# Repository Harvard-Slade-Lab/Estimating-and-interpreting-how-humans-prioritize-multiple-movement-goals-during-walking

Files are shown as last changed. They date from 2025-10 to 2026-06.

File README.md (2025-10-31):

# Estimating-and-interpreting-how-humans-prioritize-multiple-movement-goals-during-walking
Materials, data, and code needed to reproduce "Estimating and interpreting how humans prioritize multiple movement goals during walking" study.

<ins>ViPer headset materials</ins>

CAD files for the headset, Arduino code, and a BoM are included in this folder.

<ins>Data and code</ins>

Gait metrics analyzed for each step of each condition and averaged across steps are included in this folder. Code to visualize, analyze, and interpret gait metrics is included in this folder. MATLAB 2023b, Jupyter 2025.4.1, and Python 3.12.0 are required to run included code.

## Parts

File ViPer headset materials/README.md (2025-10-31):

Instructions for putting together the ViPer Headset:

1) Print motor_mirror_attachment, panel_behind_fixed_mirror, and bottom_frame using PLA.
2) Laser cut top_frame and frame_headset_interface.
3) Remove the front panel of the Google Daydream View headset.
4) Remove the insert inside the headset that rests on the face.
5) Drill four holes into the outer plastic that align with the four holes in the frame_headset_interface. The part of the headset that protrudes on the bottom should slot right into the interface.
6) Screw the frame_headset_interface onto the headset using the M2.5 screws and secure with hex nuts.
7) Assemble and secure the panel_behind_fixed_mirror, top_frame, and the frame_headset_interface with adhesives of your choice.
8) Attach the smaller mirror to the inside of the panel_behind_fixed_mirror.
9) Cover all holes with construction paper. This is an important step -- the participant's view must be obscured, but the paper ensures that it is a lightweight solution.
10) Insert M3 screw into the hole of the motor_mirror_attachment, such that it portrudes and can fit into the hole in the bottom_frame.
11) Secure the motor_mirror_attachment to the back of the large mirror with adhesives of your choice.
12) Solder the motor, the correct wires, the button, and the resistor to the Arduino UNO shield and attach it to the UNO.
13) Screw the motor onto the top of the ViPer frame using the M4 screws and secure with hex nuts.
14) Attach the motor_mirror_attachment (now attached to the large mirror) to the motor and make sure the M3 screw is dropped directly into the intended hole in the bottom_frame.
15) Secure the Arduino UNO to the top of the headset with adhesives of your choice.
17) Replace the insert inside the headset that rests on the face back inside of the headset.

Optional: If the headset feels unstable or unsecure, print the screw_tube using PLA. Align the tube with the small holes on the top and bottom of the frame next to the servo motor. Take two M2.5 screws and washers and tighten them down to either side of the tube to help hold the headset in place.

ViPer_control.ino is the script used to control the servo mounted to the ViPer headset, and it can be run through Arduino IDE.

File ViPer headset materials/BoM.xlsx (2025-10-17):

Part name | Quantity | Link to purchase | Notes
Google Daydream View headset | 1 | amazon.com/Google-Daydream-View-Headset-Slate/dp/B01N634P7O | Drill four holes to align with frame_headset_interface
Microcontroller | 1 | amazon.com/Arduino-A000066-ARDUINO-UNO-R3/dp/B008GRTSV6/ref=sxin_17_pa_sp_search_thematic_sspa?content-id=amzn1.sym.f3a06935-0d55-4a43-b918-4ea35f8505e5%3Aamzn1.sym.f3a06935-0d55-4a43-b918-4ea35f8505e5&cv_ct_cx=arduino+uno&hvadid=557574772208&hvdev=c&hvex
Servo motor | 1 | https://www.amazon.com/Leapiture-Plastic-Standard-Lightweight-Futaba/dp/B0CL6GTDXS
Large mirror | 1 | https://www.amazon.com/Plymor-Square-Non-Beveled-Glass-Mirror/dp/B0D33QFVSW
Small mirror | 1 | https://www.amazon.com/Juvale-Magnetic-Locker-Mirror-Inches/dp/B07SSSWTPN | Comes in a two pack, but only one is needed
frame_headset_interface | 1 | 3 mm acrylic, cut with laser cutter
top_frame | 1 | 3 mm acrylic, cut with laser cutter
bottom_frame | 1 | 3D printed with PLA
motor_mirror_attachment | 1 | 3D printed with PLA
panel_behind_fixed_mirror | 1 | 3D printed with PLA
M2.5 12mm socket head screws to secure headset | 4 | https://www.mcmaster.com/products/screws/thread-size~m2-5/socket-head-screws-2~/
M4 18mm socket head screws to secure motor | 4 | https://www.mcmaster.com/products/screws/socket-head-screws-2~/alloy-steel-socket-head-screws-8/?s=m4+screws
M3 20 mm socket head screw to secure mirror | 1 | https://www.mcmaster.com/products/screws/socket-head-screws-2~/alloy-steel-socket-head-screws-8/?s=m3+screws
M4 hex nuts for headset screws | 4 | https://www.mcmaster.com/products/hex-nuts/thread-size~m2-5/hex-nuts-2~~/
M4 hex nuts for motor | 4 | https://www.mcmaster.com/products/hex-nuts/thread-size~m4/hex-nuts-5~/hex-nuts-5~hex-nut-profile~standard/
Wires | 5 | https://www.amazon.com/California-JOS-Breadboard-Optional-Multicolored/dp/B0BRTJXND9 | Wires connect Arduino UNO to pushbutton
10k ohm resistor | 1 | https://www.amazon.com/EDGELEC-Resistor-Tolerance-Multiple-Resistance/dp/B07QJB31M7 | Resistor connects to pushbotton
Pushbutton | 1 | https://www.amazon.com/DAOKI-Miniature-Momentary-Tactile-Quality/dp/B01CGMP9GY | Pushbutton allows toggling between perturbation magnitudes
Proto Shield | 1 | https://www.amazon.com/HiLetgo-Prototype-Expansion-Breadboard-ProtoShield/dp/B00HHYBWPO

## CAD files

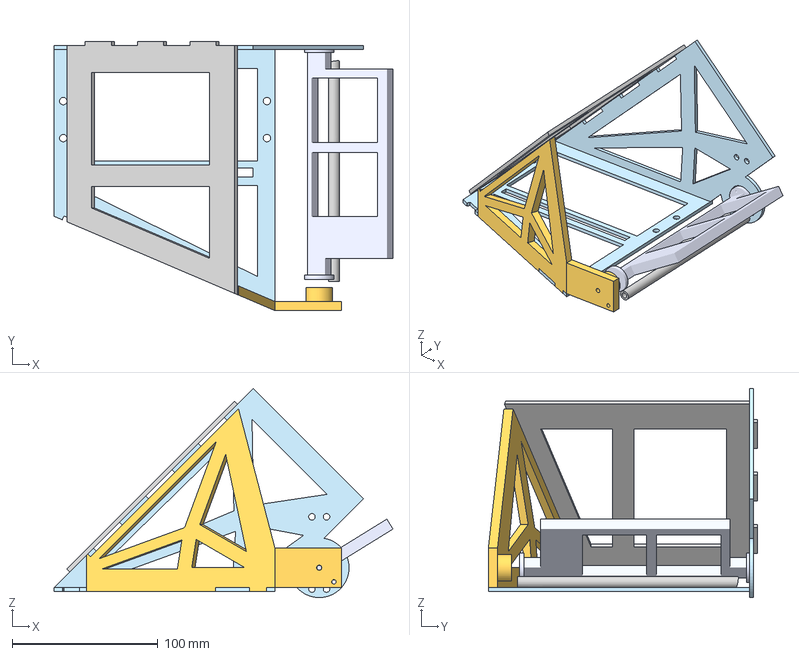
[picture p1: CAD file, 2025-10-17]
ViPer headset materials/CAD files/ViPer_Headset_assembly.step
232.5 x 184.7 x 143.4 mm
top_frame
frame_headset_interface
motor_mirror_attachment
panel_behind_fixed_mirror
bottom_frame
screw_tube

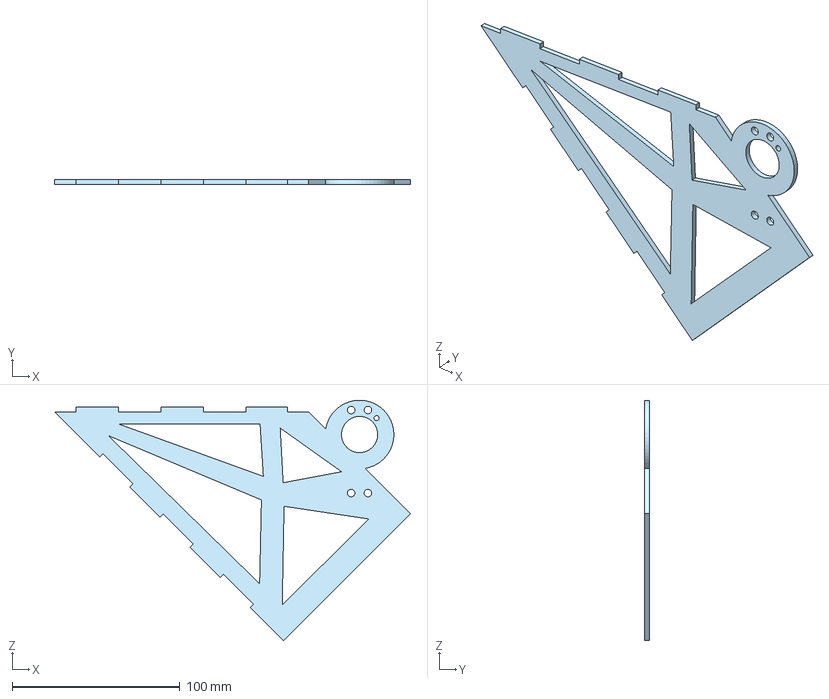
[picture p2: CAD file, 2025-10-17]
ViPer headset materials/CAD files/top_frame.step
212.3 x 2.87 x 143.4 mm

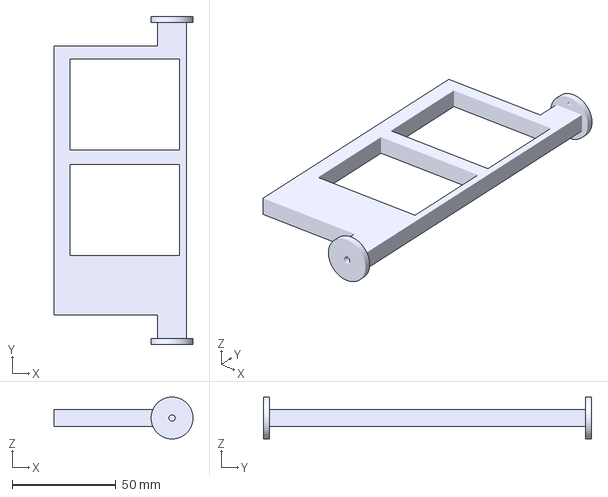
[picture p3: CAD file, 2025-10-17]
ViPer headset materials/CAD files/motor_mirror_attachment.step
67.1 x 158.5 x 20.3 mm

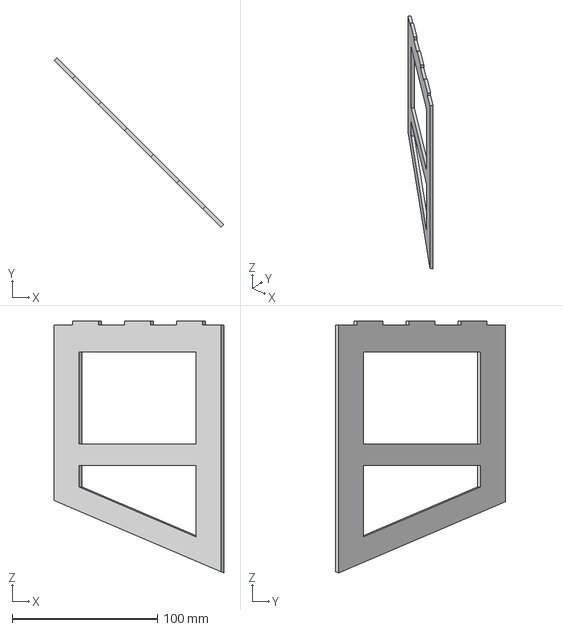
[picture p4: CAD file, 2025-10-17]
ViPer headset materials/CAD files/panel_behind_fixed_mirror.step
117.0 x 117.0 x 173.7 mm

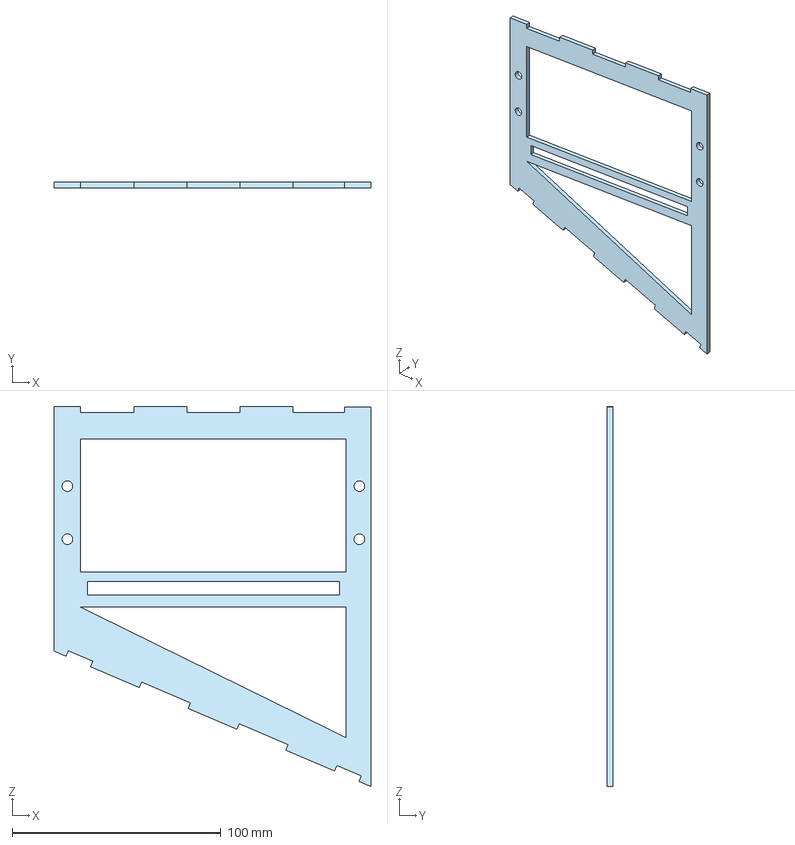
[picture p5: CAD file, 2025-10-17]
ViPer headset materials/CAD files/frame_headset_interface.step
151.5 x 2.87 x 181.8 mm

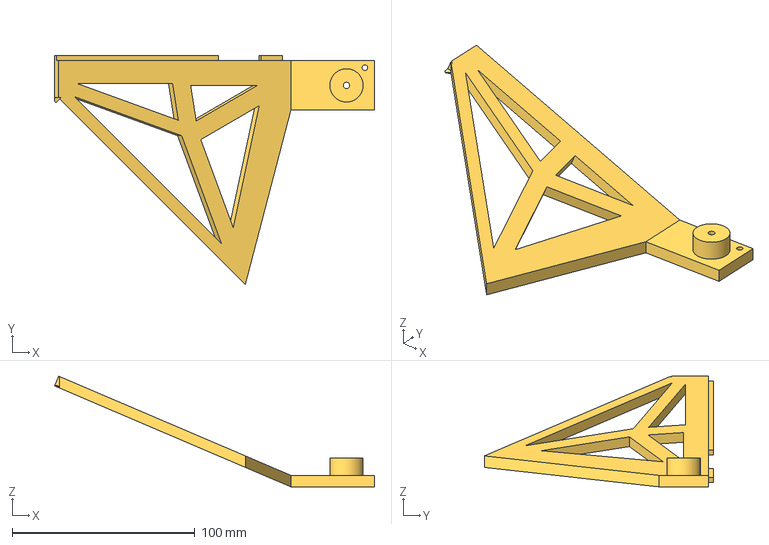
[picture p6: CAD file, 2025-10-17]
ViPer headset materials/CAD files/bottom_frame.step
175.0 x 125.4 x 60.5 mm

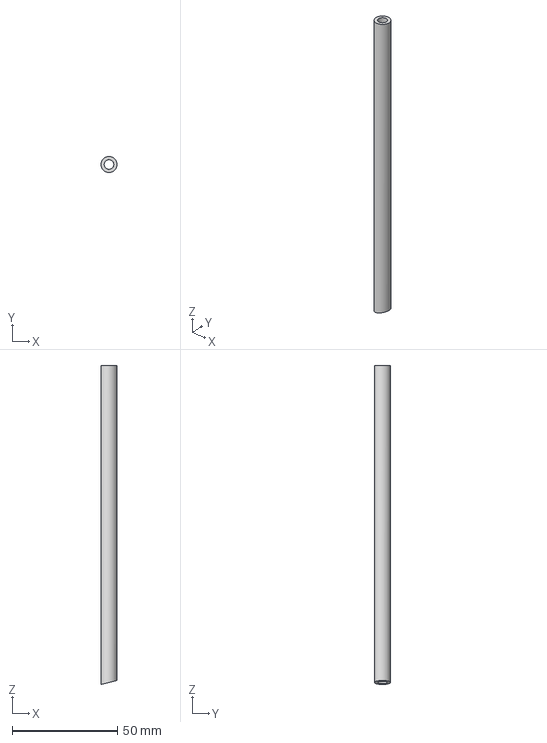
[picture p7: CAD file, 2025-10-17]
ViPer headset materials/CAD files/screw_tube.step
7.62 x 7.62 x 151.6 mm

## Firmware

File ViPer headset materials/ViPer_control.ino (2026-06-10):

#include <Servo.h>

Servo myservo;  // create servo object 

unsigned long startMillis;
const int servoPin = 10;
const int buttonPin = 2;  // button connected to pin 2
int buttonState = 0;      // current state of the button
int lastButtonState = 0;  // previous state of the button
int buttonPushCounter = 0; // counter for the number of button presses
unsigned long lastDebounceTime = 0;  // the last time the output pin was toggled
unsigned long debounceDelay = 50;    // the debounce time; increase if the output flickers
bool returningToZero = true; // flag to handle initial movement to zero position
int lastPos = 0; 

void setup() {
  Serial.begin(115200);         // initialize serial communication at 115200 bits per second
  myservo.attach(servoPin);     // attaches the servo on pin 10 to the servo object
  pinMode(buttonPin, INPUT);    // initialize the button pin as an input
  startMillis = millis();       // record the start time           // start at the neutral position
}

void loop() {

  // read the state of the switch into a local variable
  int reading = digitalRead(buttonPin);

  // check if the button state has changed
  if (reading != lastButtonState) {
    lastDebounceTime = millis(); // reset the debouncing timer
  }

  if ((millis() - lastDebounceTime) > debounceDelay) {
    // if the button state has changed:
    if (reading != buttonState) {
      buttonState = reading;

      // only toggle the counter if the new button state is HIGH
      if (buttonState == HIGH) {
        buttonPushCounter++;
        if (buttonPushCounter > 3) {
          buttonPushCounter = 0; // reset counter after 3 presses
        }
      }
    }
  }

  // save the reading. Next time through the loop, it'll be the lastButtonState:
  lastButtonState = reading;

  unsigned long currentMillis = millis();
  float t = (currentMillis - startMillis) / 1000.0;  // convert milliseconds to seconds
  float pos = 120; // default position

  // Select expression based on the number of button presses
  if (buttonPushCounter == 1) {
    // Low perturbation magnitude
    pos = 115 + 12.5*(0.5*sin(M_PI * 2 * 0.25 * t) + 0.25 * sin(M_PI * 2 * 0.125 * t) + 0.25 * sin(M_PI * 2 * 0.442 * t));
  } else if (buttonPushCounter == 2) {
    // High perturbation magnitude
    pos = 115 + 25*(0.5*sin(M_PI * 2 * 0.25 * t) + 0.25 * sin(M_PI * 2 * 0.125 * t) + 0.25 * sin(M_PI * 2 * 0.442 * t));
  } else if (buttonPushCounter == 3) {
    // Zero perturbation magnitude
    pos = 120; // Neutral
  }
//135
  // Ensure the position is within the valid range 
  pos = constrain(pos, 77, 133);

  // Only update the servo if the position has changed
  if (pos != lastPos) {
    myservo.write(pos);  // update the servo position
    lastPos = pos; // save the current position
  }
  
  myservo.write(pos);  // update the servo position
  
  // Print the position to the Serial Monitor
  Serial.print("Time: ");
  Serial.print(t);
  Serial.print(" s, Position: ");
  Serial.print(pos);
  Serial.print(" Button Presses: ");
  Serial.println(buttonPushCounter);
  
  Serial.println(pos);
  delay(15);  // small delay to smooth out the motion
}

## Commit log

2025-10-03 Create Bill of materials
2025-10-03 Rename Bill of materials to Bill of materials
2025-10-17 Add assembly instructions to README for ViPer Headset
    Added detailed assembly instructions for the ViPer Headset.
2025-10-27 Rename Step-to-step data and code/data_BMH01_test.xlsx to Step-to-step data and code/Averages per trial/data_BMH01_test.xlsx
    [data_BMH01_test.xlsx]
2025-10-27 Rename Step-to-step data and code/data_BMH02_test.xlsx to Step-to-step data and code/Averages per trial/data_BMH02_test.xlsx
    [data_BMH02_test.xlsx]
2025-10-27 Rename Step-to-step data and code/data_BMH06_test.xlsx to Step-to-step data and code/Averages per trial/data_BMH06_test.xlsx
    [data_BMH06_test.xlsx]
2025-10-27 Rename Step-to-step data and code/data_BMH07_test.xlsx to Step-to-step data and code/Averages per trial/data_BMH07_test.xlsx
    [data_BMH07_test.xlsx]
2025-10-27 Rename Step-to-step data and code/data_BMH08_test.xlsx to Step-to-step data and code/Averages per trial/data_BMH08_test.xlsx
    [data_BMH08_test.xlsx]
2025-10-27 Rename Step-to-step data and code/data_BMH09_test.xlsx to Step-to-step data and code/Averages per trial/data_BMH09_test.xlsx
    [data_BMH09_test.xlsx]
2025-10-27 Rename Step-to-step data and code/data_BMH10_test.xlsx to Step-to-step data and code/Averages per trial/data_BMH10_test.xlsx
    [data_BMH10_test.xlsx]
2025-10-27 Rename Step-to-step data and code/data_BMH13_test.xlsx to Step-to-step data and code/Averages per trial/data_BMH13_test.xlsx
    [data_BMH13_test.xlsx]
2025-10-27 Rename Step-to-step data and code/data_BMH17_test.xlsx to Step-to-step data and code/Averages per trial/data_BMH17_test.xlsx
    [data_BMH17_test.xlsx]
2025-10-27 Rename Step-to-step data and code/data_BMH19_test.xlsx to Step-to-step data and code/Averages per trial/data_BMH19_test.xlsx
    [data_BMH19_test.xlsx]
2025-10-27 Rename Step-to-step data and code/data_BMH20_test.xlsx to Step-to-step data and code/Averages per trial/data_BMH20_test.xlsx
    [data_BMH20_test.xlsx]
2025-10-27 Rename Step-to-step data and code/data_BMH21_test.xlsx to Step-to-step data and code/Averages per trial/data_BMH21_test.xlsx
    [data_BMH21_test.xlsx]
2025-10-31 Update README with ViPer_control.ino details
    Added information about the ViPer_control.ino script for Arduino.
